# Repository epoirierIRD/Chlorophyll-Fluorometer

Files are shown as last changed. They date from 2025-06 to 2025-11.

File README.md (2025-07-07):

<p align="center">
  ENSSAT Logo
</p>

# Chlorophyll-Fluorometer

## Description

This project aims to develop a portable and low-cost fluorometer for detecting chlorophyll-a concentration, a key indicator of phytoplankton presence. The project is conducted by students in photonics from Enssat in collaboration with the European Institute for Marine Studies (IUEM) and is part of an open-source initiative to facilitate easy and cost-effective replication of the device.

This GitHub repository contains all the necessary resources and instructions for making the device.

The document [Fluoremeter overview](Fluorometer_overview.pdf) aims to provide an overview of the technical aspects of our fluorometer.

## Features

- Measures chlorophyll-a concentration in the range of [1-50] µg/L.
- Low-cost (approximately $200), low-tech, and open-source design.
- Portable

## Principle of fluorometry

<p align="center">
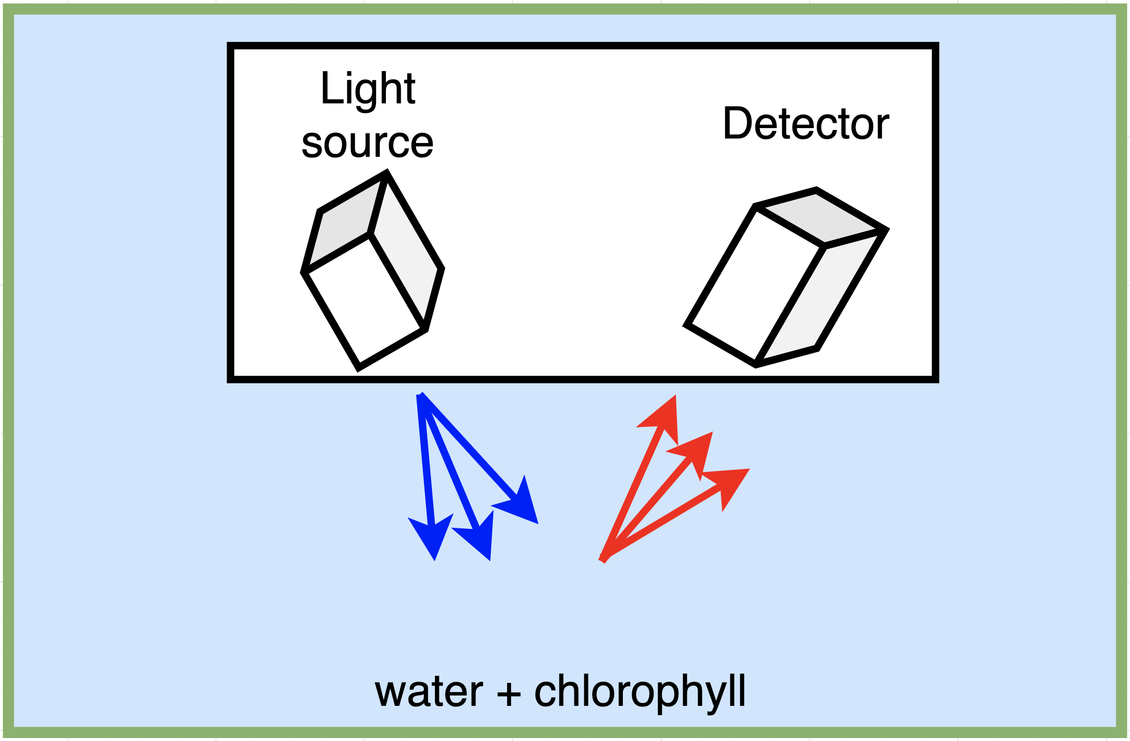
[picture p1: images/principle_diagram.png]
principle diagram
  
</p>

The principle of fluorometry is based on the fact that chlorophyll-a in phytoplankton, when excited by a blue light source at a wavelength of 430 nm, re-emits light in the red spectrum around 670 nm. This red fluorescence is detected by a photodetector, enabling the measurement of chlorophyll-a concentration in the sample.

## Functionality

<p align="center">
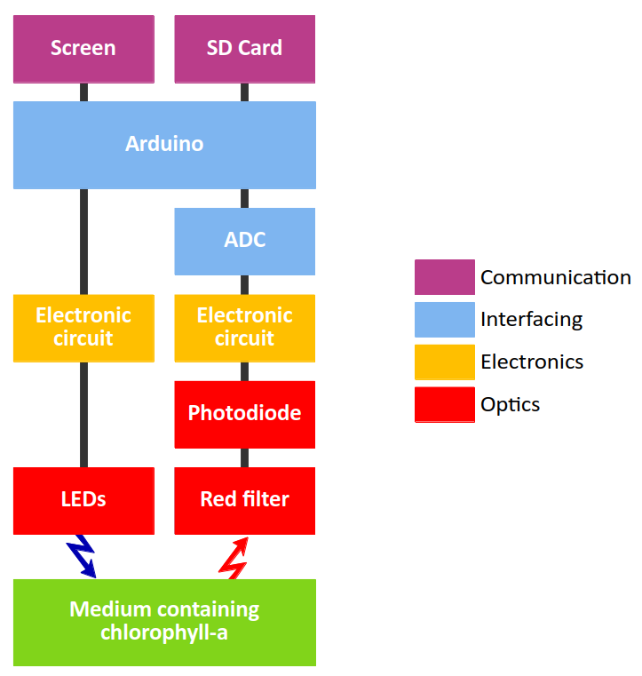
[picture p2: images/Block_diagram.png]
Block diagram
  
</p>

With our setup, high sensitivity is achieved by usind two LEDs and a large-area photodiode to collect more efficiently fluorescence. A red filter is used to prevent the detection of wavelengths other than red. The Arduino board enables modulation and demodulation to eliminate ambient red light.

## Components

The main components are:

| Component | Description |
|-----------|-------------|
| LED | Light Emitting Diode for blue excitation |
| Photodiode | Detects red fluorescence |
| Arduino | Microcontroller for processing |
| ADC | Analog to Digital Converter |
| Transistor | For LED power supply |
| Amplifier | For signal enhancement|
| OLED Screen | Displays values |
| SD Card Shield | Saves values in an SD Card |

For a detailed list of components with the references, please refer to the [Components List](hardware/components.md).

## Construction of the fluorometer

### Prerequisites

- Arduino IDE
- Electronic components
- 3D printer
- Soldering equipment
- Laser cutter

### Installation Steps

1. **Clone the Repository:**

   ```bash
   git clone https://github.com/EnssatPhotonicsProjects/Chlorophyll-Fluorometer.git
   ```

### Assembling the fluorometer

Follow the steps of the [assembly guide](assembly_guide.md) to build the fluorometer.

<p align="center">
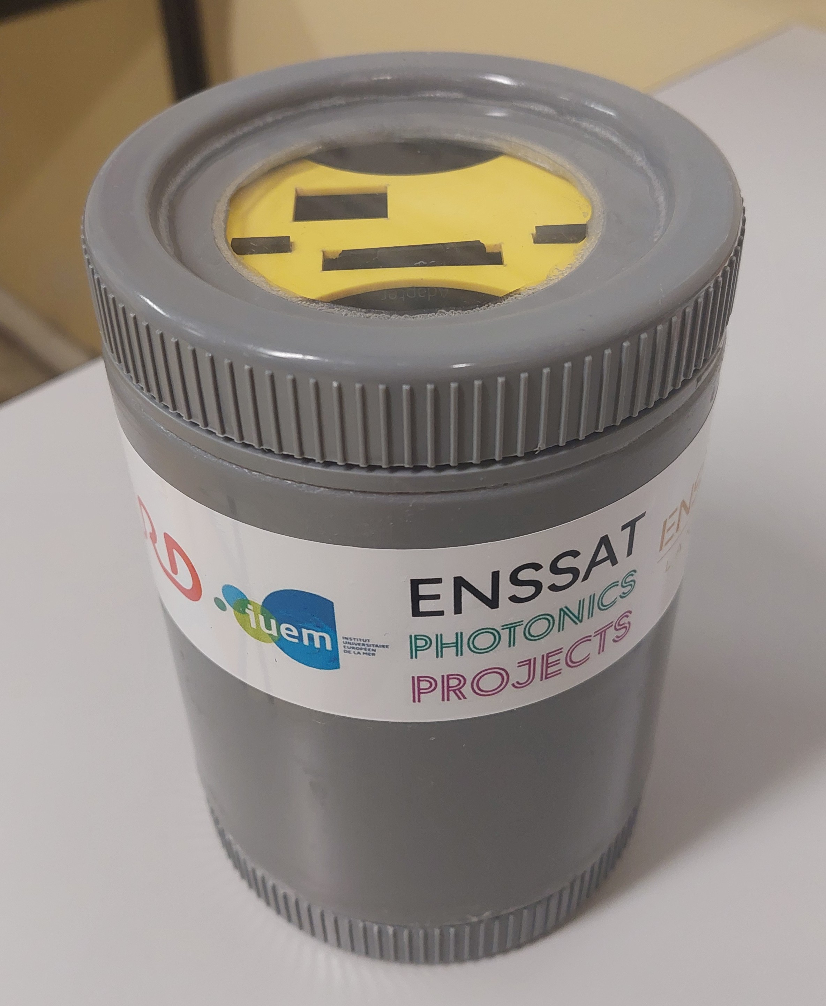
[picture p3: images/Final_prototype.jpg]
Final prototype
  
</p>

## Avenues for Improvement

- The photodiode becomes saturated when used outdoors in bright light.
- The PVC box may not withstand high pressure underwater.

Contributions are welcomed to improve these points.

## To contribute

Contributions to this project are welcomed. Follow this procedure contribute:

1. **Fork the repository** and create your branch:

   ```bash
   git checkout -b my-new-feature
   ```

2. **Make your changes** and test them thoroughly.

3. **Document your changes** in the [EXTERNAL_CONTRIBUTIONS](EXTERNAL_CONTRIBUTIONS.md) file. Begin the file with your name, location and date.

4. **Submit a Pull Request** with a detailed description of your changes.

## Contributors

Team 2024-2025 :
- Loïc Goumarre (minimadcap)
- Cécile Plaçais (CecileP28)
- Agathe Douissard (Douidoui2)
- Olivier Josephiak (Josephiak)
- Mayssame Ismael (Goulgoul1)
- Hugo Le Moal (HugoLeMoal)
- Viken Tevonian
- Merlin Rivière

Team 2023-2024 :
- Jérémy Gigandet
- Brice Hervé
- Thomas Quinchon
- Damien Depauw
- Etienne Chaillot
- Nicolas Chabrier
- Thomas Gysemberg

## Acknowledgments

The authors warmly thank Thierry Chartier, Laurent Bramerie, supervisors of the project at Enssat, Philippe Laborie (Laboratoire de physique corpusculaire, Caen, France) and Etienne Poirier (IUEM, Plouzané, France), members of the steering committee, for their advice and support throughout the project. Special thanks to Etienne Poirier for giving the idea of the project, trusting us and welcome us at IUEM in the last days of the project.

Authors are also very grateful to Antoine Courtay, Hervé Daniel, Clément Dauphin, Hervé Chuberre, teachers at Enssat, and Jean-Philippe Lesault, technician at Enssat, for their advice and technical support. Special thanks to Yvan Guilloit, in charge of the MakerSpace at IUT de Lannion, France, for his help in the integration of the device in the waterproof box.

The fluorometer project started in september 2023 with a first team of Enssat students. Our fluorometer could not have been finalized without their initial work. Many thanks to Nicolas Chabrier, Etienne Chaillot, Damien Depauw, Jérémy Gigandet, Thomas Gysemberg, Brice Hervé, and Thomas Quinchon.

We had the chance to meet Michel Hignette (oceanographer and president of ArmorScience, Lannion, France). We are very grateful to him for sharing his knowledge on phytoplankton.

Hence, we would like to thank Maël Guibré (student at IUT de Lannion) for the time he took to make some videos of the project.

## License

This project is licensed under [CC BY-SA 4.0]. Please see the [`LICENSE`](LICENSE.md) file for more details.

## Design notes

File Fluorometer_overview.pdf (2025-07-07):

# A portable, low-cost, low-tech and open source fluorometer for the measurement of chlorophyll-a concentration

Lo¨ıc Goumarre, C´ecile Pla¸cais, Agathe Douissard, Viken Tevonian, Olivier Josephiak, Mayssame Ismael, Hugo Le Moal and Merlin Riviere

Enssat, 6 rue de Kerampont 22300 Lannion, France, www.enssat.fr, photonics.projects@enssat.fr.

4 July 2025

## 1 Introduction

Chlorophyll-a concentration is a key indicator to estimate the phytoplankton biomass in aquatic ecosystems. Measurements of such concentrations can be made with a fluorometer. Its operating principle is to illuminate the water medium with a blue light and to measure the red fluorescence of chlorophyll-a. However, on today’s market, commercially available fluorometers are quite expensive (several thousands of euros typically) and bulky. For the scientific community, there is a strong need to develop portable and cost-effective solutions, and a very active research is carried out in this area [1, 2, 3, 4, 5].
We are a team of students in photonics at Enssat, Lannion, France, and we took part in a collaborative project between Enssat and the Institut Universitaire Europ´een de la Mer (IUEM, European Institute For Marine Studies). This project meets IUEM’s need to create a portable, low-cost, low-tech, and open source chlorophyll-a concentration sensor. The highly-sensitive device we have successfully developped is affordable (around 200 e) and easily reproducible thanks to the detailed documentaton available on GitHub [6].
The present document aims to provide an overview of some technical aspects of our fluorometer. It first presents the background and specific requirements of the project (defined in collaboration with the IUEM). The design of the fluorometer is then presented, with separate sections in optics, electronics and interfacing. Finally, we present the results of tests carried out with our fluorometer.

## 2 Needs

The IUEM provided us detailed specifications describing the needs and requirements for the development of the fluorometer. This sensor had to be portable, low-cost, low-tech and open source. The specifications served as the basis for guiding the design and the development of the chlorophyll-a concentration sensor, meeting standard requirements for environmental monitoring.
The technical specifications expected for the sensor in terms of metrology were the following:
Range | [0.1-50] µg/L
Measurement sensitivity | 0.1 µg/L
Measurement error | < 0.2 µg/L

The electronical specifications were:

Measurement rate | 10 sec
Response time | 1 sec
Alimentation | 3.3 V, 5 V or 12 V
Data output protocol | I2C, UART or analog

## 3 General principle

When chlorophyll-a is excited by a blue light source at a wavelength of about 430 nm, it re-emits light in the red spectrum around 670 nm. This red fluorescence is collected by a photodetector, enabling the concentration of chlorophyll-a to be measured. Figure 1(a) illustrates the absorption and emission spectrum of chlorophyll-a, and figure 1(b) shows a schematic diagram of a fluorometer.

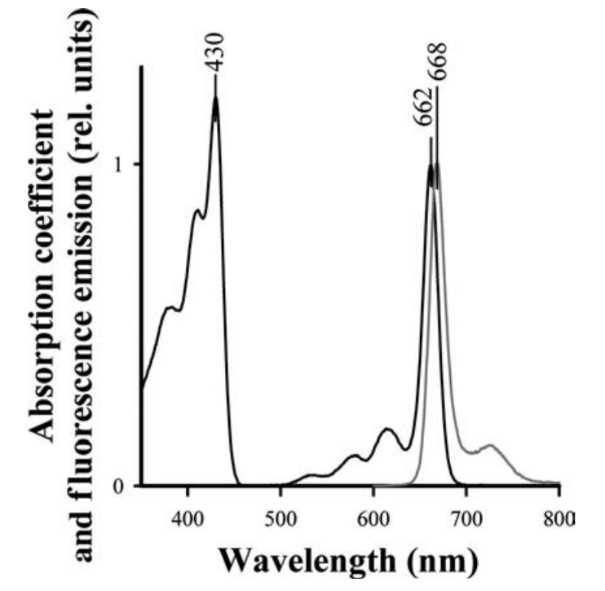
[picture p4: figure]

(a) Absorption and emission spectrum of chlorophyll-a.

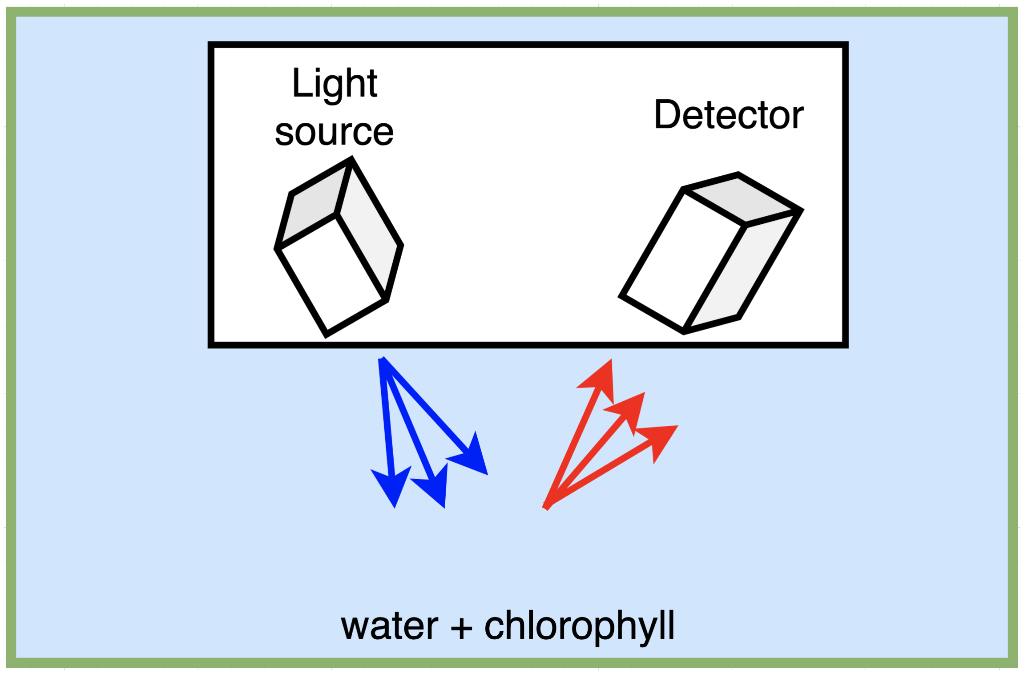
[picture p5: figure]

(b) Schematic diagram of a fluorometer.

Figure 1: Principle of fluorimetry with chlorophyll-a.

## 4 Fluorometer conception

### 4.1 Block diagram

Figure 2 illustrates the block diagram of our fluorometer. Blue LEDs illuminate the water medium containing chlorophyll-a. A photodiode detects the red fluorescence of chlorophyll-a through a red filter used to prevent the detection of light at other wavelengths than red. The Arduino board enables modulation and demodulation to eliminate ambient red light.

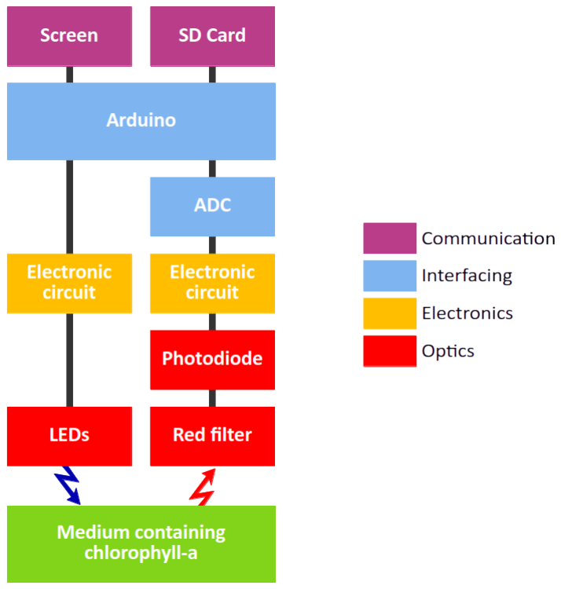
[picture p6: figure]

Figure 2: Block diagram.

The different parts shown in the block diagram of figure 2 will now be detailed.

### 4.2 Optical part

The optical part of our project is divided into two sub-parts : emission and reception.

### 4.2.1 Emission

As explained previously, a blue LED is needed to make a chlorophyll-a fluoremeter. We actually used two LEDs to double the available optical power. Specifications of the LEDs are given in table 1.

Reference | Luxeon C Color Line - Violet
Peak wavelength | 424 nm (measured)
Spectral half-width | 20 nm
Typical viewing angle | 165°
Typical power | 600 mW

Table 1: Specifications of the blue LEDs.

Due to their large viewing angle, we performed measurements to find the optimum angle between the LEDs and the photodiode. Figure 3 shows the measured voltage on the photodiode as a function of the angle between one LED and the photodiode in an experimental setup similar to figure 1(b). It shows that the optimal angle is around 30°. In the following, the photodiode will be positioned parallel to the air-water interface and the two LEDs will be on either side of the photodiode at an angle of 30°, as depicted later in figure 5.

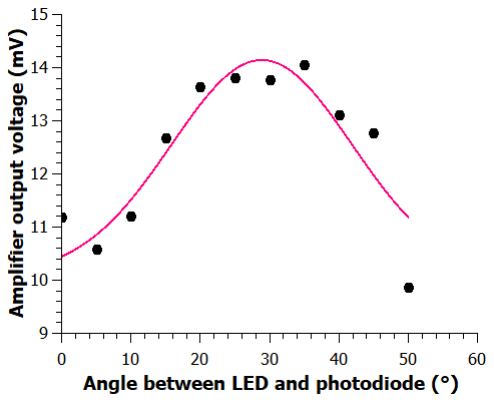
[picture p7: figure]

Figure 3: Amplifier output voltage on the photodiode as a function of the angle netween the LED and the photodiode.

### 4.2.2 Reception

Once the chlorophyll-a is stimulated with blue light, it fluoresces red light. This red light is collected by a photodiode positioned against the transparent window of the fluorometer to capture maximum fluorescence. A photodiode with a large area maximizes the collected light. However, it is also important to take into account the dark current of the photodiode. The dark current must be sufficiently low to detect low chlorophyll concentrations. The specifications of the choosen photodiode are presented in table 2.

Reference | Thorlabs FDS10X10
Dark current | 200 pA
Surface | 100 mm²

Table 2: Specifications of the photodiode.

Three layers of a red filter are placed in front of the photodiode to filter out other wavelengths than red. The red filter we use is a light filter used by lighting technicians in the entertainment industry. Its specifications are described in table 3. The transmission spectrum of the filter is shown in figure 4. The red filter of 3D glasses can also be used for example.

Reference | Lee Filters 164 Flame Red
Colour temperature | 6774 K
Transmission at 424 nm | 3 %
Transmission at 670 nm | 79 %

Table 3: Specifications of the red filter.

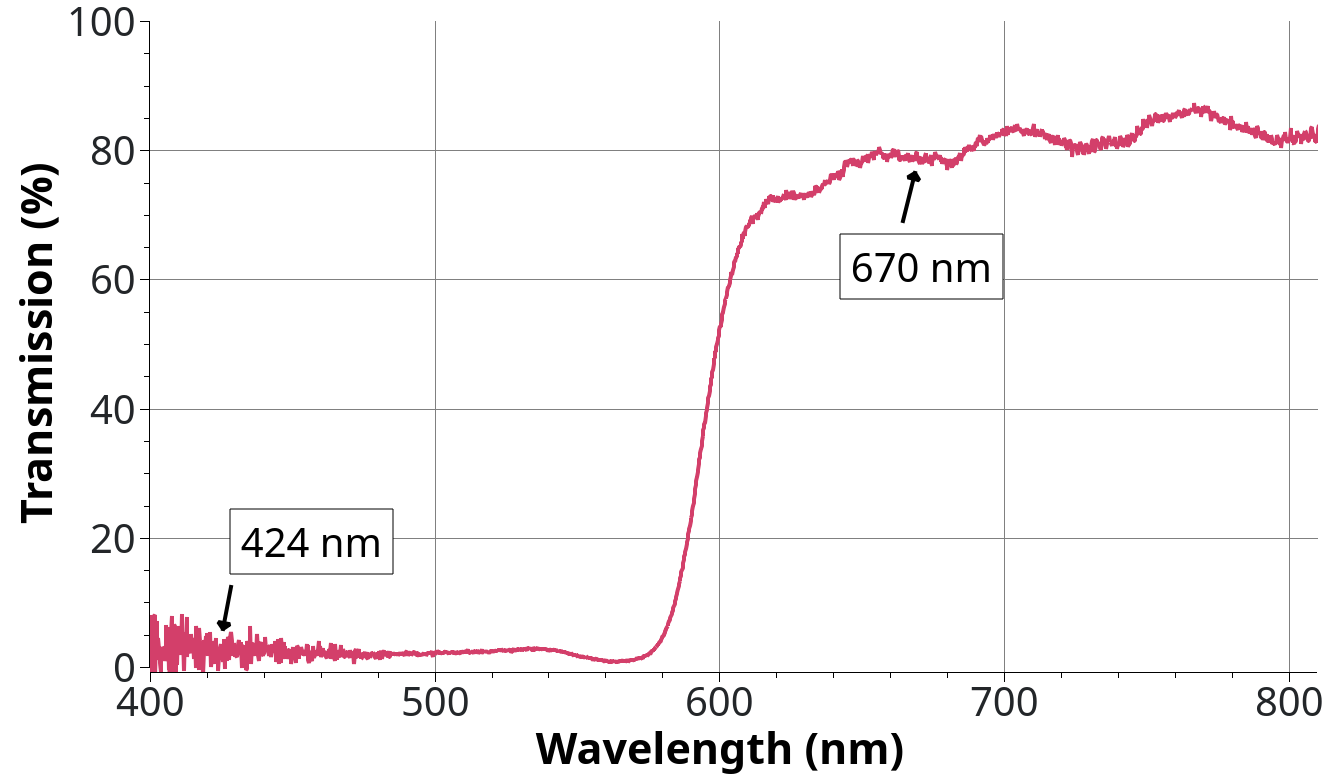
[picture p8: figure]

Figure 4: Transmission spectrum of the red filter.

The final setup for the optical components is shown in Figure 5.

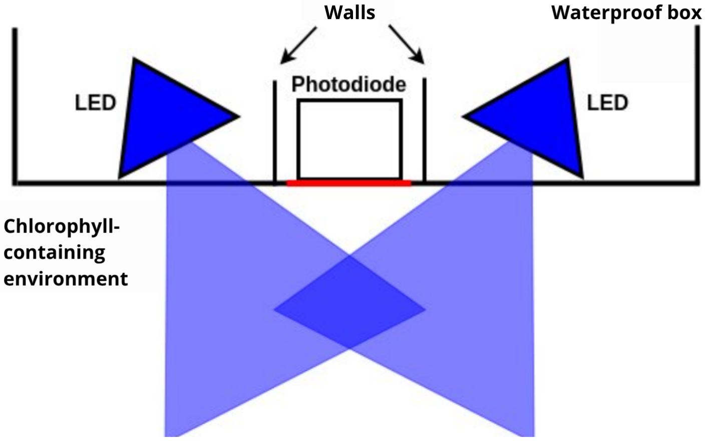
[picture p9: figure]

Figure 5: Final configuration of the optical components.

### 4.3 Electronical part

In this section, we describe the different electronic circuits present in our device.

### 4.3.1 LEDs alimentation

First, the two LEDs have to be powered with a current of 400 mA each. To do that, we propose the electric circuit of figure 6. The transistor provides the current that powers the LEDs. It is controlled by the desired voltage. The transistor transforms this voltage into a current that is shared equally between the two LEDs. The specifications of the transistor are presented in table 4.

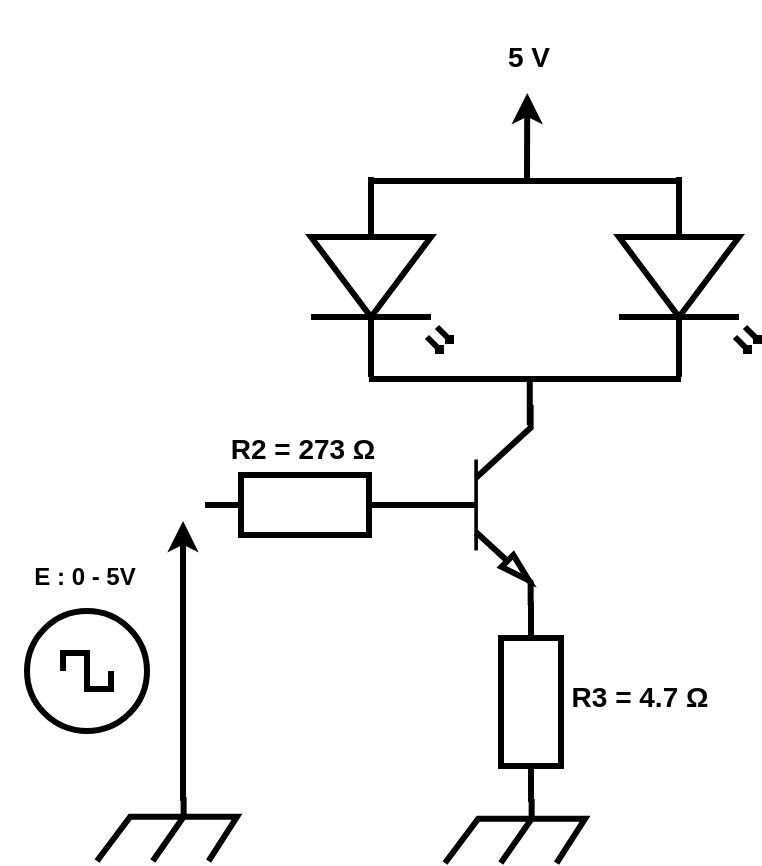
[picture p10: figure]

Figure 6: Circuit diagram of the LEDs alimentation.

Reference | PN2222
Type | BJT n-type
VCE (sat) | 1 V
VBE (sat) | 2 V
hFE | between 100 and 300

Table 4: Specifications of the transistor.

### 4.3.2 Transimpedance amplifier

For the receiving part of the device, the transimpedance amplifier of figure 7 is proposed. Thanks to this amplifier, the photodiode current is converted into a voltage up to Vmax = 5 V in order to be read by an analog-to-digital converter (ADC). The amplifier gain corresponds to the value of R1 and is 10⁵ V/A in our case. This indicates that the maximum measurable photocurrent is Imax = Vmax/R1 = 50 µA. In the absence of additionnal noise source, the minimum measurable photocurrent is theoretically the dark current of the phototodiode, i.e. 200 pA in our case.

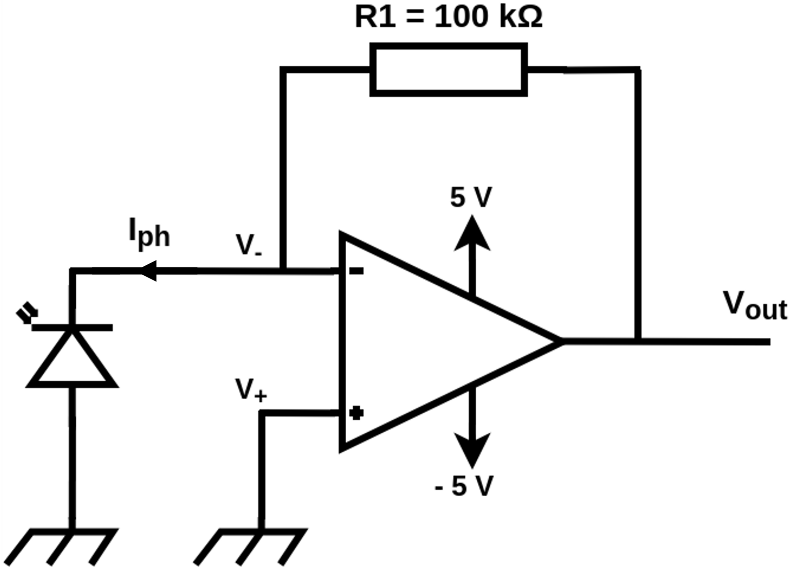
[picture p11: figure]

Figure 7: Circuit diagram of the transimpedance amplifier.

### 4.3.3 Generation of −5/0/+5 V

Self-sufficient power supply (typically a powerbank) can be ideal to power the fluorometer. However, this kind of battery provides only a 0-5 V voltage. To generate the −5/0/+5 V voltage needed by the operational amplifier of figure 7, we use the switched capacitor voltage converter (MAX660) shown in figure 8.

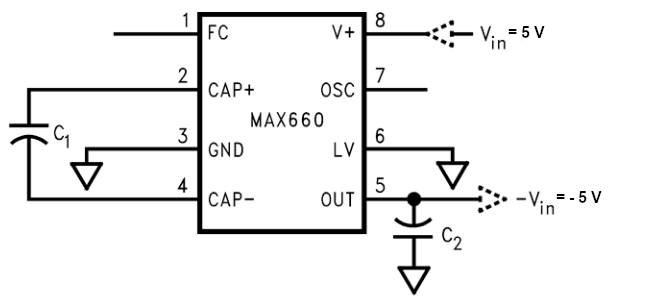
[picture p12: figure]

Figure 8: Switched capacitor voltage converter (MAX660) for −5/0/+5 V generation.

### 4.4 Interfacing part

### 4.4.1 Modulation of the LEDs

The blue light emitted by the LEDs is on-off modulated by the Arduino at a frequency of 100 Hz and a duty cycle of 1/2. This modulation is maintained during 1 s, then the LEDs are switched off for 9 s. The time diagram of the modulation scheme is shown in figure 9. The modulation frequency of the LEDs is limited by the execution time of the Arduino program.

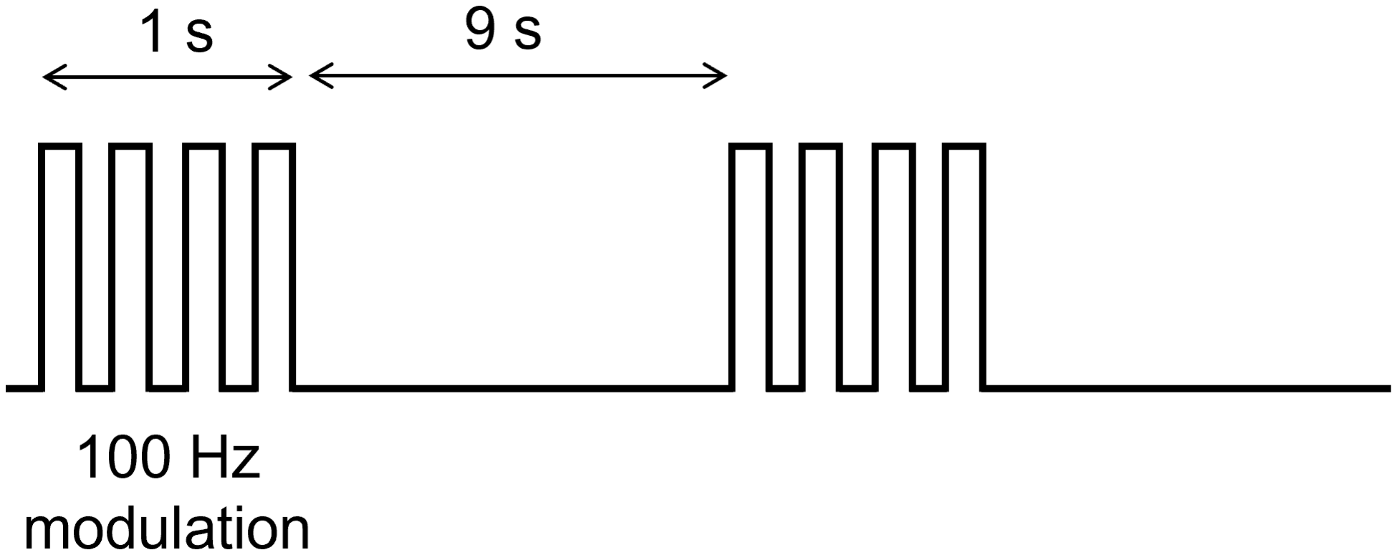
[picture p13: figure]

Figure 9: Modulation time diagram.

### 4.4.2 Analog-to-digital conversion

The Arduino board we use is the UNO R3. Its internal ADC is a 12-bit ADC. To increase the resolution of our fluorometer, we prefer to use an external ADC (ADS 1115) with a 16-bit sampling. Thus, the resolution of the fluorometer is 76 µV per bit, corresponding to 0,76 nA per bit.

### 4.4.3 Demodulation

To demodulate the signal, the program reads the photodiode voltage during both the on-state and the off-state of the LEDs during the flashing phase of 1 s. Then it substracts the off-state voltage Voff from the on-state voltage Von in order to eliminate the ambiant red light. This ensures to measure only the fluorescence of the chlorophyll due to the blue excitation. Figure 10 summaries the demodulation process.

Then the programme averages the 100 values calculated during the 100 periods of the flashing phase and returns one single value of photocurrent every 10 s.

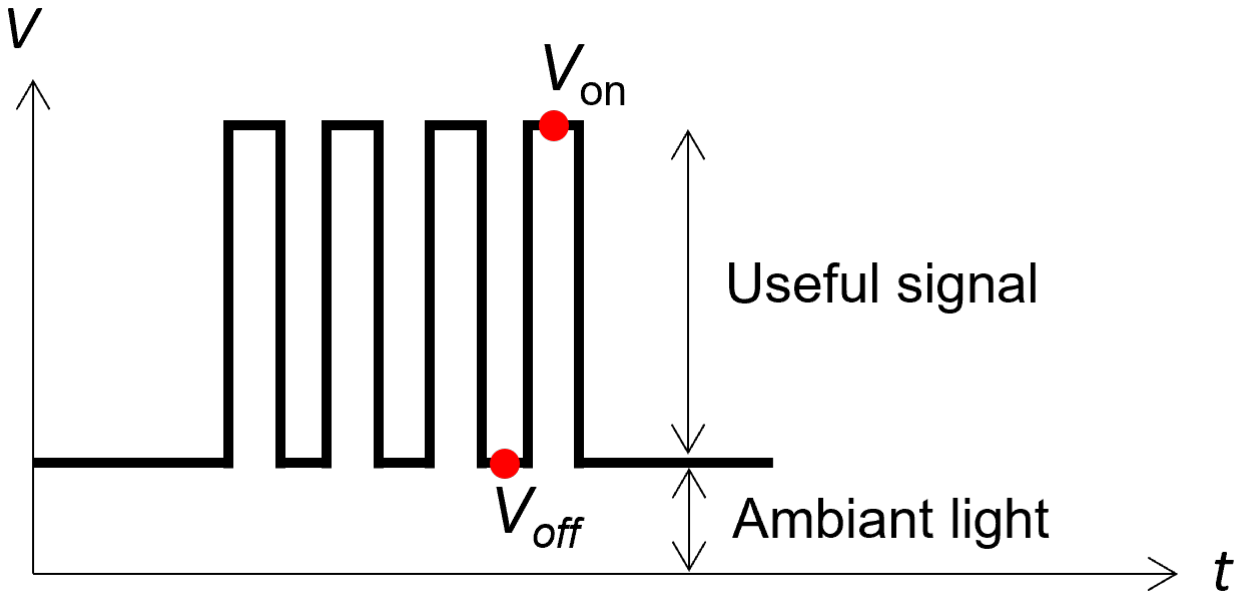
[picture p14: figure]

Figure 10: Demodulation of the received signal.

### 4.4.4 Display and storage

A OLED screen is added to facilitate interactions with the users. It displays the values of the measured photocurrent in nA.
A SD card shield is also added for long-term recording. The photocurrent values, as well as the time of measurement, are recorded on the SD card in the form of a text file, as shown in figure 11.

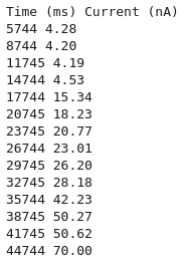
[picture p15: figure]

Figure 11: Text file recorded on the SD card.

### 4.5 Final diagram

The global circuit diagram of the fluorometer is shown in figure 12.

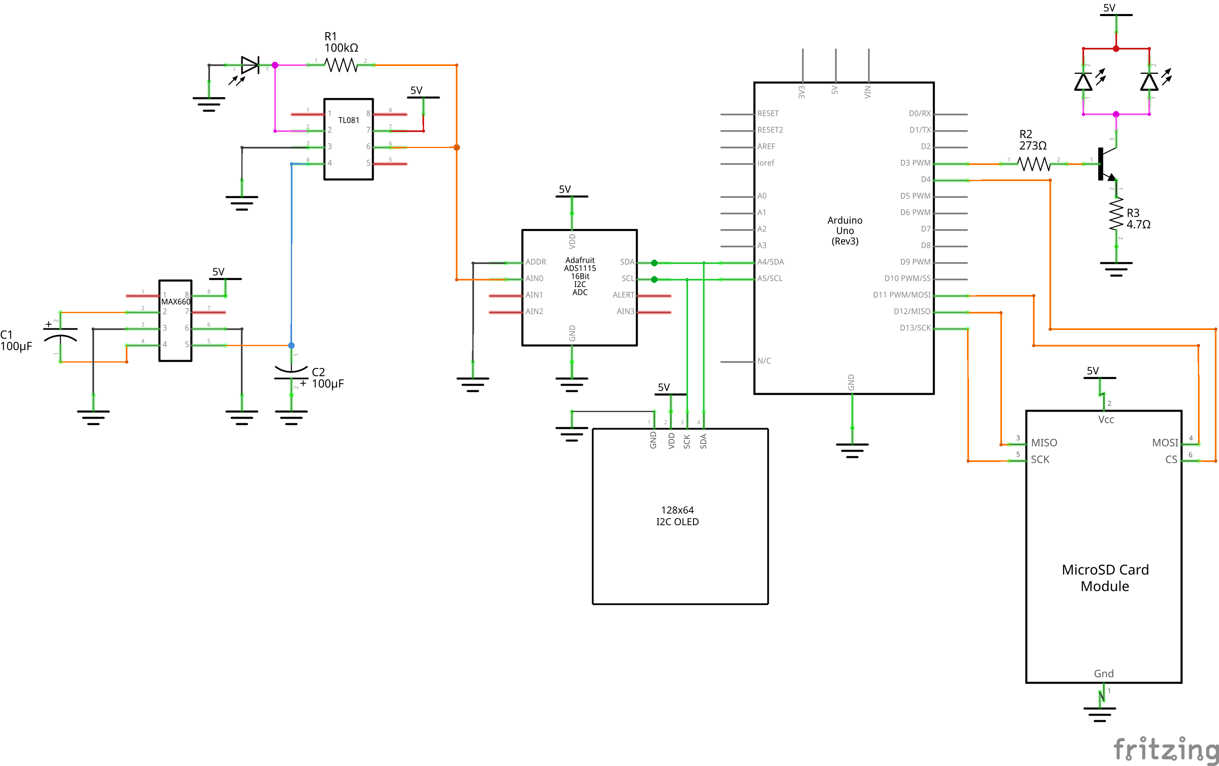
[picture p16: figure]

Figure 12: Fluorometer’s global circuit diagram.

### 4.6 Final Assembly

The fluorometer is assembled in a PVC tube. Access plugs are glued to the ends of a sleeve. The caps are cut out and a transparent plate of PMMA plastic is glued on to let the light going through. The inner structure that holds the Arduino and the circuit board is made in black PMMA and cut with a laser cutter. Spacers are used to strengthen the structure. The holder for the LEDs and the photodiode is 3D-printed and screwed to the structure. A powerbank is added in the box for the autonomy of the system.
The bottom cap is glued and cannot be opened. The top cap can be opened and the structure is easy to remove in order to recharge the powerbank, take the SD card, load a program on the Arduino or replace a component. The complete box is waterproof. Yet, PVC box may not withstand high pressure underwater.

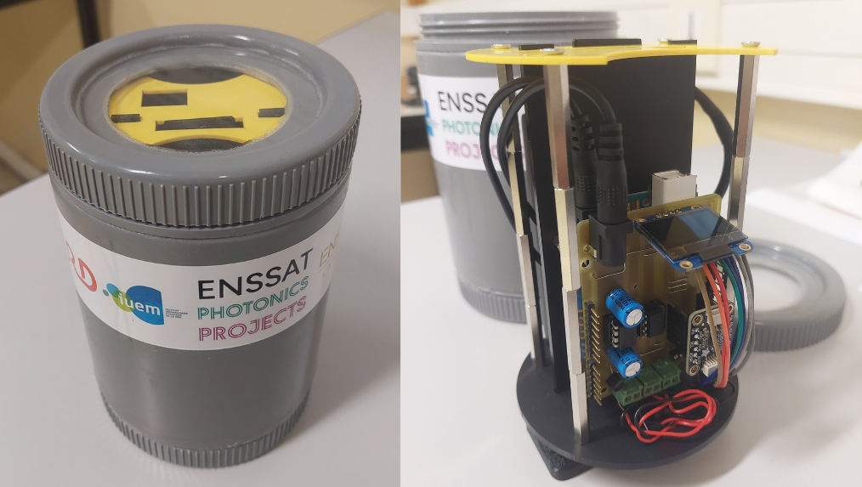
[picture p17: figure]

Figure 13: Photos of the prototype.

## 5 Tests and results

A series of tests were carried out to caracterize and calibrate the fluorometer.

### 5.1 Measurements with spinach chlorophyll-a

Firstly, measurements of solutions of chlorophyll-a extracted from spinach leaves have been made. The spinach chlorophyll-a was extracted following this method : spinach leaves have been shredded and the chlorophyll-a filtered using 96% ethanol. Then the concentration has been measured with a spectrometer thanks to the formula demonstrated in [7]. These measurements were done in a dark room. The results are shown in figure 14.

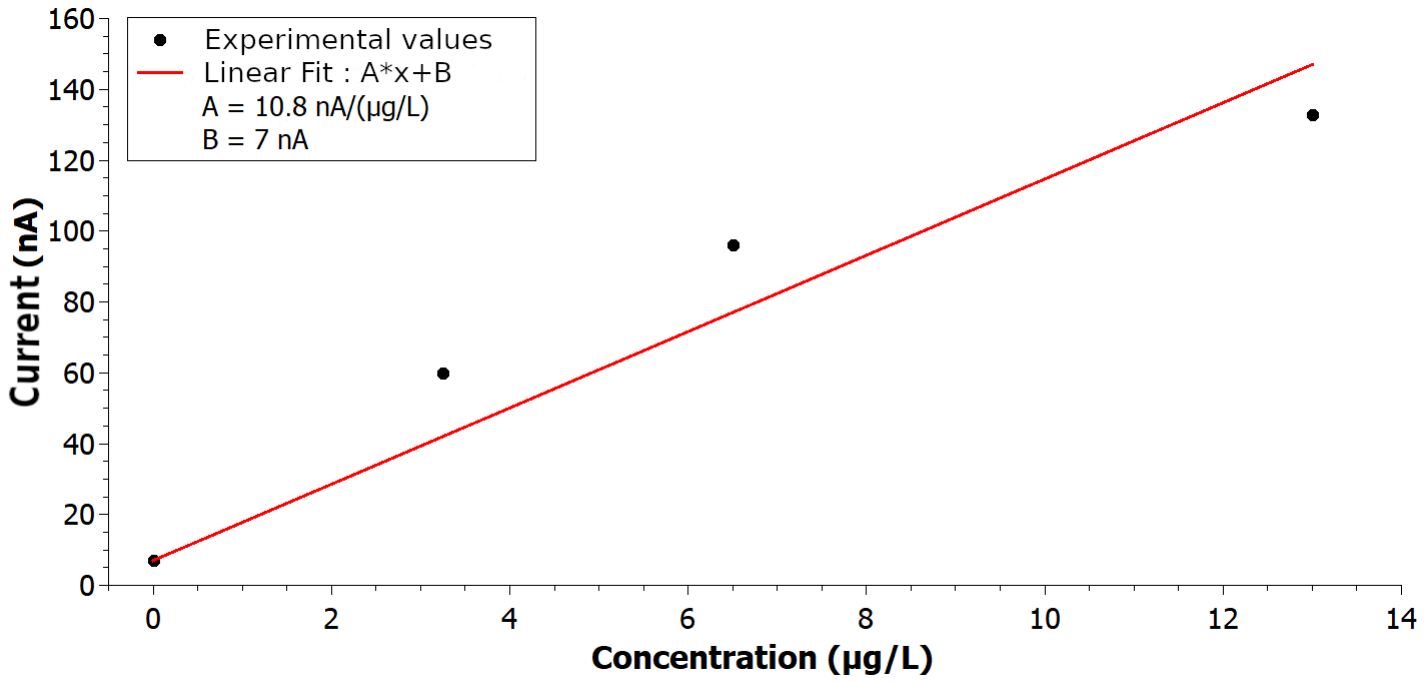
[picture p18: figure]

Figure 14: Calibration of the fluorometer with spinach chlorophyll-a.

This calibration shows that the fluorometer can measure low concentrations of chlorophyll. The first point, corresponding to 7 nA, is a measurement in clear water. This gives the detection threshold of our prototype. This value is not the 200 pA dark current of the photodiode because of other noise sources (due do electronics for example).

### 5.2 Measurements with phytoplankton

Then, measurements of solutions of phytoplankton have been run with our fluorometer. A highly concentrated phytoplankton solution has been diluted. Values of concentration were measured with a commercial fluorometer (the RBRtridente) and the corresponding current was read on our low-cost fluorometer. Figure 15 shows the results.

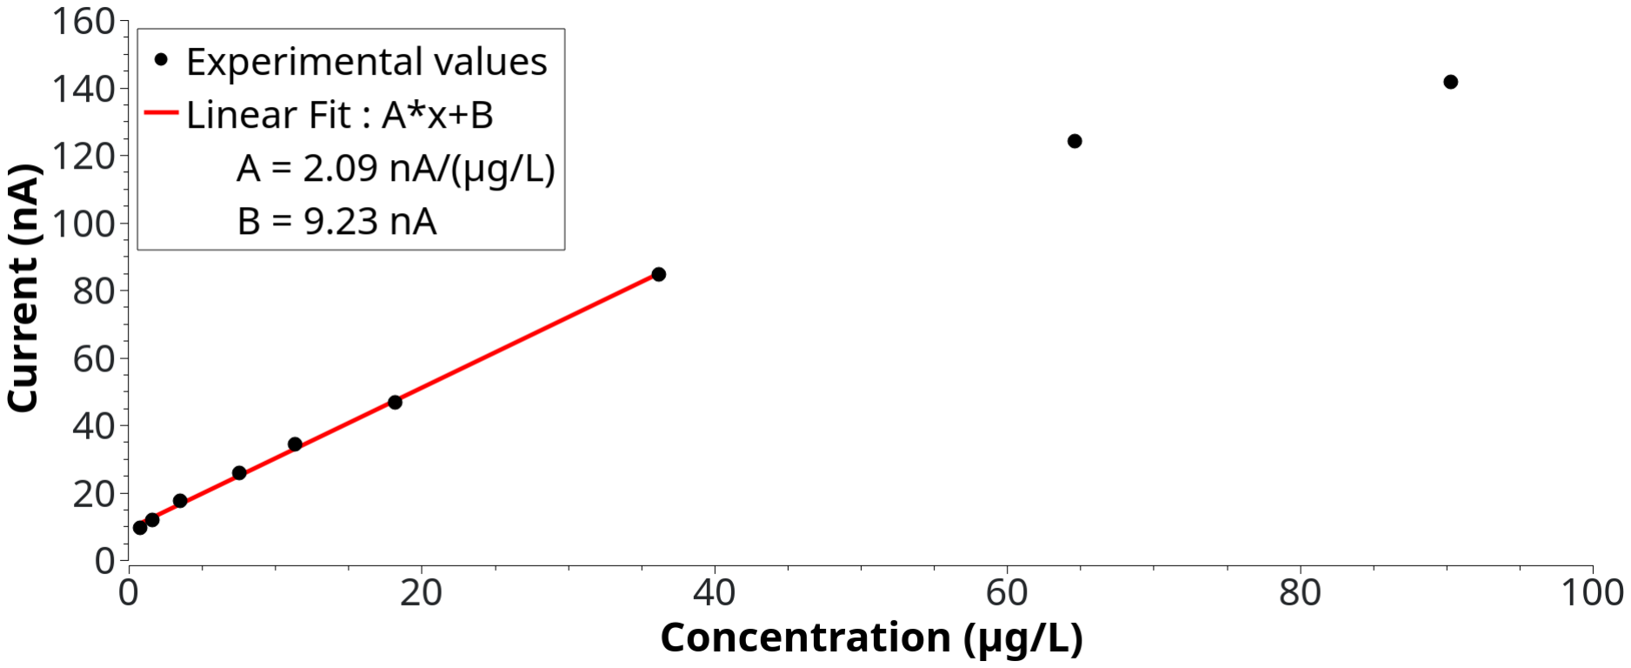
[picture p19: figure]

Figure 15: Calibration of the fluorometer with phytoplankton.

The fluorometer operates linearly over a range from 1 to 50 µg/L. The interesting point is that our fluorometer can measure chlorophyll-a concentrations as low as 1 µg/L under experimental laboratory conditions. The prototype is limited to indoor use, as the photodiode saturates outdoors in bright light.

## 6 Conclusion

During this project, we have realised a fluorometer for chlorophyll-a concentration measurements. This fluorometer is portable, low-cost and low-tech. It can be completely reproductible thanks to a public GitHub repository [6].
Our fluorometer can measure chlorophyll-a concentrations as low as 1 µg/L. This performance is achieved thanks to the use of two blue LEDs illuminating a large volume of water and a large-area photodiode with a low dark current. Our fluorometer is simple, low-cost (around 200 e) and easy to make thanks to the use of standard components. In the context of global warming, the need to measure phytoplankton is crucial. Portable and low-cost solutions might play a very important role in the future for diagnosing the ecological status of aquatic environments. We sincerely hope that our solution can help the scientific community, and would be delighted to make a small contribution to environmental protection through the study of coastal zones.

## Acknowledgments

The authors warmly thank Thierry Chartier, Laurent Bramerie, supervisors of the project at Enssat, Philippe Laborie (Laboratoire de physique corpusculaire, Caen, France) and Etienne Poirier (IUEM, Plouzan´e, France), members of the steering committee, for their advice and support throughout the project. Special thanks to Etienne Poirier for giving the idea of the project, trusting us and welcome us at IUEM in the last days of the project.
Authors are also very grateful to Antoine Courtay, Herv´e Daniel, Cl´ement Dauphin, Herv´e Chuberre, teachers at Enssat, and Jean-Philippe Lesault, technician at Enssat, for their advice and technical support. Special thanks to Yvan Guilloit, in charge of the MakerSpace at IUT de Lannion, France, for his help in the integration of the device in the waterproof box.
The fluorometer project started in september 2023 with a first team of Enssat students. Our fluorometer could not have been finalized without their initial work. Many thanks to Nicolas Chabrier, Etienne Chaillot, Damien Depauw, J´er´emy Gigandet, Thomas Gysemberg, Brice Herv´e, and Thomas Quinchon.
We had the chance to meet Michel Hignette (oceanographer and president of ArmorScience, Lannion, France). We are very grateful to him for sharing his knowledge on phytoplankton.

Hence, we would like to thank Ma¨el Guibr´e (student at IUT de Lannion) for the time he took to make some videos of the project.

## References

[1] T. Leeuw et al., In situ Measurements of Phytoplankton Fluorescence Using Low Cost Electronics, Sensors, Vol. 13, pp. 7872–7883 (2013). https://www.mdpi.com/1424-8220/13/6/7872.
[2] Harvey Bates et al., A guide to Open-JIP, a low-cost open-source chlorophyll fluorometer, Photosynthesis Research, Vol. 142, pp. 361–368 (2019). https://doi.org/10.1007/s11120-019-00673-2.
[3] L. R. C. S´a, et al., Portable and Low-Cost Fluorometer for Phytoplankton Monitoring, 2023 IEEE 7th Portuguese Meeting on Bioengineering (ENBENG), pp. 96–99 (2023). https://ieeexplore.ieee.org/document/10175351.
[4] R. Sanchez Olvera, D´eveloppement d’une sonde multiparam`etres `a bas coˆut pour les eaux marines et continentales, Th`ese de doctorat de l’Universit´e Toulouse III - Paul Sabatier (2024). https://theses.fr/2024TLSES108.
[5] X. Chen et al. A low-cost and portable fluorometer based on an optical pick-up unit for chlorophyll-a detection, Talanta, Vol. 269, pp. 125447. https://doi.org/10.1016/j.talanta.2023.125447.
[6] https://github.com/EnssatPhotonicsProjects/Chlorophyll-Fluorometer.
[7] J.F.G.M. Wintermans and A. De Mots, Spectrophotometric characteristics of chlorophylls a and b and their pheophytins in ethanol, Biochimica et Biophysica Acta (BBA) - Biophysics including Photosynthesis, Vol. 109, pp. 448-453 (1965). https://doi.org/10.1016/0926-6585(65)90170-6.


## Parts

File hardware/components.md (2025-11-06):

# List of components for EU based project

## Electronic components

| Component | Manufacturer - Ref | Seller - Ref | Quantity | Price per unit (€) |
|-----------|---------------------|--------------|----------|--------------------|
| Photodiode | Thorlabs - FDS10X10 | [Thorlabs - FDS10X10](https://www.thorlabs.com/thorproduct.cfm?partnumber=FDS10X10) | 1 | 122 € |
| Arduino | ARDUINO UNO SMD R3 ATMEGA328 - A000073 | [Mouser - A000073](https://www.mouser.fr/ProductDetail/782-A000073) | 1 | 22 € |
| ADC 16 bits | ADS1115 Adafruit I2C - ADA1085 | [GoTronic - 31893](https://www.gotronic.fr/art-module-4-canaux-analogiques-i2c-ada1085-21114.htm) | 1 | 19.90 € |
| LED[¹] | Luxeon C Color Line - Violet 420-430 nm L1C1-VLT1000000000 | [LED-Supply, Vermont USA](https://www.ledsupply.com/leds/luxeon-c-color-leds) | 2 | 6 $ |
| Red Filter | Lee Filters - 182 Light Red | [La BS - FL182](https://www.la-bs.com/ArticleDetails.aspx?Code=FL182) | 1 | 20 € |
| Transistor | PN2222A TRANS NPN 40V 0.8A TO-92-3 PN2222A PBFREE | [Mouser 610-PN2222A](https://www.mouser.fr/ProductDetail/610-PN2222A) | 1 | <1 € |
| Operational amplifier | TL081 | [Mouser - 595-TL081CP](https://www.mouser.fr/ProductDetail/595-TL081CP) | 1 | <1 € |
| 8 contacts socket | IC & Component Socket, 8 Contacts, DIP Socket, 2.54 mm, 7.62 mm, Copper Alloy, DILB8P-223TLF | [ Farnell - 2668407 ](https://fr.farnell.com/en-FR/amphenol-icc-fci/dilb8p-223tlf/dip-socket-8pos-2row-2-54mm-th/dp/2668407) | 2 | 0.2 € |
| Wire-To-Board Terminal Block | 3.5 mm, 2 Ways, 30 AWG, 16 AWG, 1.5 mm², Screw, Phoenix 1751248 | [Farnell - 2478586](https://fr.farnell.com/en-FR/phoenix-contact/mkds-1-2-3-5/tb-wire-to-brd-2pos-16awg/dp/2478586) | 3 | 1.3 € |
| Voltage converter | MAX660 MAX660CPA+ | [Mouser 700-MAX660CPA](https://www.mouser.fr/ProductDetail/700-MAX660CPA) | 1 | 8.39 € |
| Resistors 100 kΩ brown black yellow gold | Through Hole Resistor, 100 kohm, 250 mW, ± 1%, Axial Leaded, 250 V| [Farnell - 9341129](https://fr.farnell.com/en-FR/multicomp-pro/mf25-100k/res-100k-1-0-25w-axial-metal-film/dp/9341129) | 1 | 0.10 € |
| Resistors 270 Ω red violet brown gold | Through Hole Resistor, 270 ohm, MCF Series, 250 mW, ± 5%, Axial Leaded, 250 V, MCF 0.25W 270R | [Farnell - 9339353](https://fr.farnell.com/en-FR/multicomp-pro/mcf-0-25w-270r/res-270r-5-250mw-axial-carbon/dp/9339353) | 1 | 0.04€ |
| Resistors 4.75 Ω +/- 1% yellow violet green silver brown | Through Hole Resistor, 4.7 ohm, MF25 Series, 250 mW, ± 1%, Axial Leaded, 250 V, MF25 4R7 | [Farnell - 9341994](https://fr.farnell.com/en-FR/multicomp-pro/mf25-4r7/res-4r7-1-250mw-axial-metal-film/dp/9341994) | 1 | 0.12 € |
| Capacitor 150 μF, 16V | Electrolytic Capacitor, 150 µF, 16 V, ± 20%, Radial Leaded, 2000 hours @ 105°C, Polar | [Farnell - 3131982](https://fr.farnell.com/wurth-elektronik/860020373008/condensateur-150uf-16v-alu-elec/dp/3131982) | 2 | 0.16€ |
| OLED Screen 128x64 Dot Matrix | DFRRobot DFR0650 SSD1306 | [Mouser - DFR0650](https://www.mouser.fr/ProductDetail/DFRobot/DFR0650?qs=vmHwEFxEFR9nN6dqGZZLUA%3D%3D) | 1 | 13.05 € |
| SD Card Shield | TRU COMPONENTS TC-8579888 | [GoTronic - 28506](https://www.gotronic.fr/art-module-carte-sd-gt126-28506.htm) | 1 | 9.49 € |
| Powerbank[²] | Output 5 V - 2.4 A, dim. 100 x 50 x 25 mm max | [VRURC 2000mAh mini power bank](https://www.amazon.fr/gp/product/B099F29H7Y?smid=A2BNE5LRDUXQ6R&th=1) | 1 | 30 € |
| Alimentation cable part 1 | Power splitter 5.5 x 2.1 mm CA50-2 | [Gotronic 49105](https://www.gotronic.fr/art-dedoubleur-d-alimentation-5-5-x-2-1-mm-ca50-2-24581.htm) + angled USB plug (homemade) | 1 | 2.65 € |
| Alimentation cable part 2 | USB cable male A right angled + USB male A | [TL494-ND Digikey UR020-006-RA](https://www.digikey.fr/fr/products/detail/eaton-tripp-lite/UR020-006-RA/4767696) | 1 | 7.85 € |
| DC Power Connector| DC10A, Jack, 5 A, 2.1 mm, PCB Mount, Solder, CLIFF FC68148  | [Farnell 224959](https://fr.farnell.com/en-FR/cliff-electronic-components/fc68148/conn-dc-power-jack-2-1mm-5a-12v/dp/224959?CMP=GRHB-OCTOPART) | 1 | 6.57 € |

[¹]LED-Supply does not have a reseller in Europe for integrated LED on PCB. LED and PCB(eval-board) can be bought separately from European reseller and assembled. References to come shortly  
[²]Several options are possible for the power bank, Lipo battery,... geometric dimensions are critical due to littel space available. Beware, there is litlle power demand and some powerbanks shut down automatically.

## Case and support

| Component | Reference | Quantity | Price per unit |
|-----------|-----------|----------|----------------|
| Filament PLA black | / | **not determined** | ≈5 € |
| PVC sleeve | 100 mm diameter | 1 | 2 € |
| PVC plug | 100 mm diameter | 2 | 7.58 € |
| Transparent PMMA thickness 3 mm | / | ~400 cm² | 2 € |
| Matt black PMMA thickness 3 mm | / | ~180 cm² | 1 € |
| PMMA thickness 2 mm | / | ~100 cm² | <1 € |
| Screws, nuts, washers, spacers | / | ~50 pcs | 10 € |

## Final price

The price is estimated in **June 2025** at **230 $ without delivery**.

The price is estimated in **July 2025** at **300 € without delivery**.

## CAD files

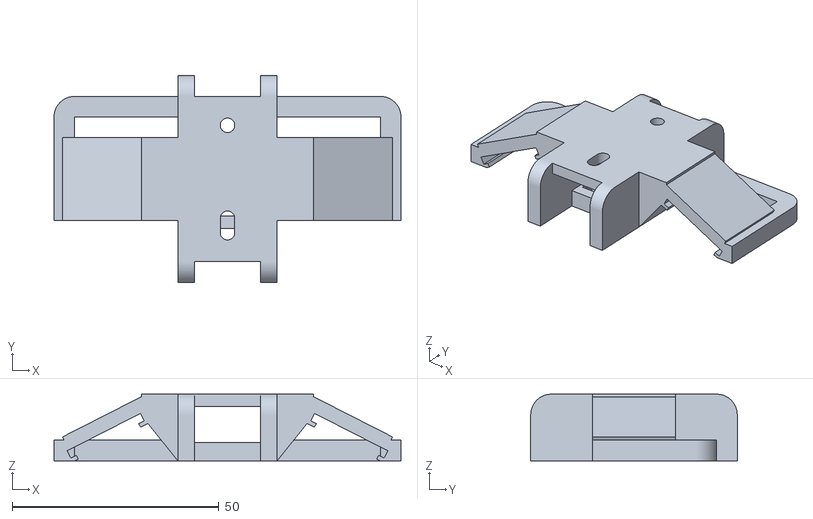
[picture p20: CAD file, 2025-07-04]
hardware/3D_ready_to_print_LED-Photodiode-Support.stl
84.0 x 50.0 x 16.2

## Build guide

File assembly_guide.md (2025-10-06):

# Assembly Guide for Chlorophyll-Fluorometer

This guide provides detailed instructions on how to assemble the Chlorophyll-Fluorometer device.

## Prerequisites

Before starting the assembly process, ensure you have the following tools and components ready:

- Arduino IDE installed on your computer
- All electronic components listed in the [Components List](hardware/components.md)
- 3D printer for printing support structures
- Soldering equipment for assembling electronic circuits
- Basic hand tools (screwdrivers, pliers, etc.)

## Step 1: Clone the Repository

To get started, clone the project repository to your local machine:

```bash
git clone https://github.com/EnssatPhotonicsProjects/Chlorophyll-Fluorometer.git
```

## Step 2: Assemble the Electronic Components

### Using a Breadboard

If you are prototyping or prefer not to use a PCB, you can assemble the circuit on a breadboard. Refer to the [Circuit-diagram.pdf](hardware/Circuit-diagram.pdf) for detailed connections.

### Using a PCB

1. Download the PCB design file from the repository: [PCB File](hardware/Fluorometer_PCB/).
2. Order the PCB from a manufacturer or print it if you have the necessary equipment. For example, go to [JLCPCB](https://jlcpcb.com/), and in the field "Add gerber files" drop a zip of the folder /CAMoutputs situated at [this location](hardware/Fluorometer_PCB/).
You will receive a quality pro PCB and you can even choose the color.
3. Solder the components onto the PCB following the schematic diagram. 
Tip: As you will solder with you PCB upside down, start with the thin components (resistors,...) and finish with the thick ones (headers, capacitor, ...).

## Step 3: Assemble the Support Structures

Use the provided STL file to 3D print the necessary support structures with black PLA filament, and a filling density of 50%. Printing takes about 7 hours : 

- [LED and Photodiode Support](hardware/3D_ready_to_print_LED-Photodiode-Support.stl)

Assemble the parts according to the instructions provided in the [Assembly Manual](structure_assembly_guide.md).

## Step 4: Upload the Arduino Code

1. Open the `.ino` file in the Arduino IDE.
2. Connect your Arduino board to the computer.
3. Select the correct board and port in the Arduino IDE.
4. Upload the code to the Arduino board.

## Step 5: Calibration

Follow the calibration protocol described in the [Calibration Guide](calibration.md) to ensure accurate measurements:

1. Prepare the calibration standards.
2. Adjust the device settings according to the calibration data.
3. Verify the calibration by testing with known samples.

## Troubleshooting

If you encounter any issues during the assembly or operation of the device, open an issue in the repository.

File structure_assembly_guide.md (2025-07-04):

# Assembly Guide for Support Structures

This guide provides detailed instructions on how to assemble the Chlorophyll-Fluorometer structures.

## Prerequisites

Before starting the assembly process, ensure you have the following tools and components ready:

- Components from the [Components List](hardware/components.md)
- PVC glue
- Sandpaper
- PVC stripper
- Laser cutter
- Screws, nuts, washers, spacers
- Paper towel or rag
- Wires (red and black)
- Soldering station

## Step 1 : Assemble the LEDs and photodiode support

Start by soldering wires to the LEDs and photodiode terminal. Pay attention to the polarity of the terminals : you can solder a red wire on the + terminals of the LED and the cathode terminal of the photodiode. A black wire can be soldered on the - terminals of the LEDs and on the anode of the photodiode.

When this is done, you can assemble de following components :
- Two LEDs
- Photodiode
- (Red filter : 16 x 20 mm) X3
- 3D printed support

<p align="center">
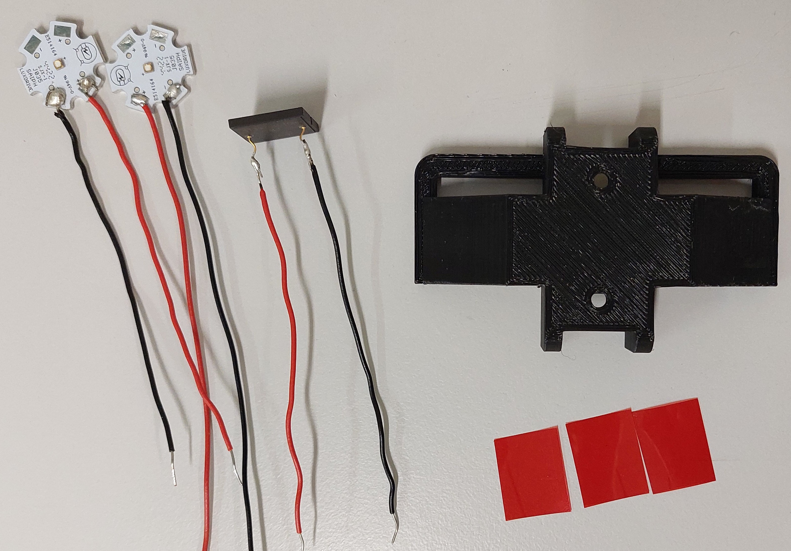
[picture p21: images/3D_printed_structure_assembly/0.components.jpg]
0.components
  
</p>

1. Position the LEDs in their slots. If they don't fit, you can lightly file the LEDs bases. The LEDs must be perfectly held by the support and must not move. The wires must come out of the back of the bracket.

<p align="center">
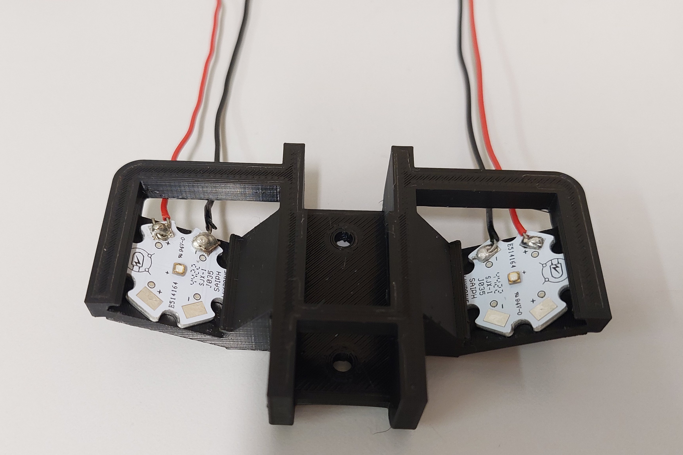
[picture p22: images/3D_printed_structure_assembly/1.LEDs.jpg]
1.LEDs
  
</p>

2. Position the photodiode in its slot. Bend the wires to make them come out of the back of the bracket.

<p align="center">
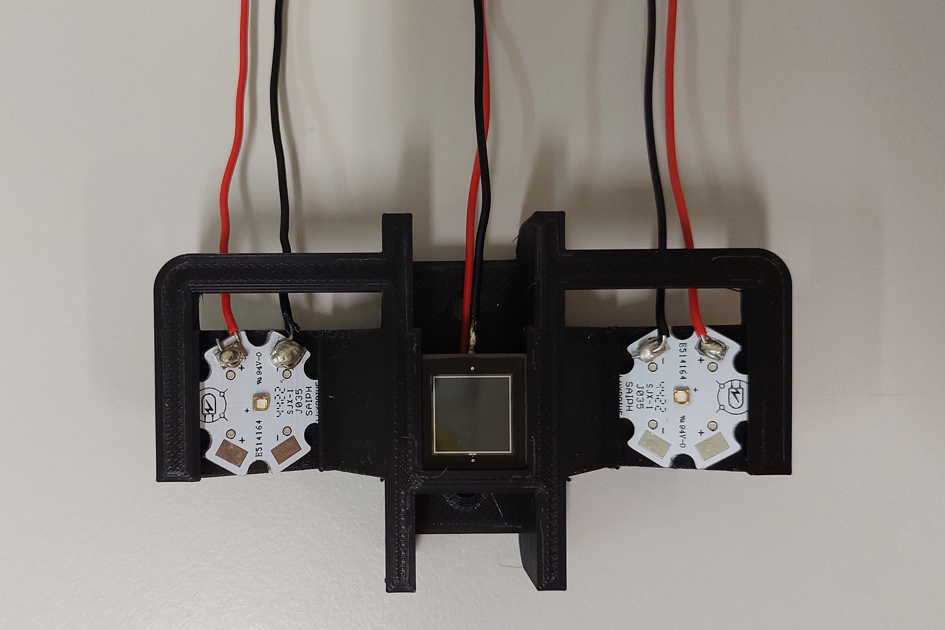
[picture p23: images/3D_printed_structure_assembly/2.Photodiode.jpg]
2.Photodiode
  
</p>

3. Add the three pieces of red filter. You can slide them in the photodiode slot, this will hold everything in place in the holder. However, make sure that the filters are perfectly flat on the photodiode, or light could pass underneath. You can add a small piece of scotch tape to the end of the filters and fold it over the photodiode so that nothing escapes.

<p align="center">
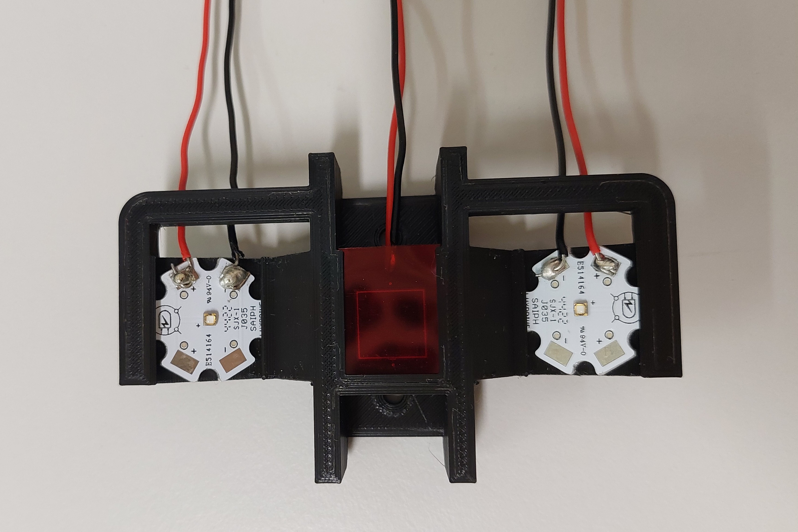
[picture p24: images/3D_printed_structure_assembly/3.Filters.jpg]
3.Filters
  
</p>

## Step 2 : Assemble the internal structure

The materials required for this step are :
- The Arduino UNO R3 board
- The PCB board with all the electronic components (Screen, SD Card shield)
- 4 spacers of 5 mm
- 4 screws, diameter 3 mm, length 5 mm + nuts
- 16 spacers of 30 mm
- 4 countersunk screw, diameter 3 mm, length 8 mm + nuts + washers
- 2 screws, diameter 3 mm, length 10 mm + nuts + washers
- 2 screws, diameter 2 mm, length 12 mm + nuts + washers
- A powerbank (100 x 50 x 2.5) mm max
- A dual output power supply and angled USB output cable
- The LEDs and photodiode support made in the previous step
- Matt black PMMA sheet, thickness 3 mm
- PMMA sheet, thickness 2 mm
- Screwdriver
- Laser cutter

<p align="center">
  0.components
</p>

1. Cut the structure in the PMMA sheets with the laser cutter. In 2 mm PMMA, cut the [top plate](hardware/Ready_to_laser_cut_Top-Plate.svg). In black PMMA, cut the [face and bottom plates](hardware/Ready_to_laser_cut_Structure-Plans.svg).

<p align="center">
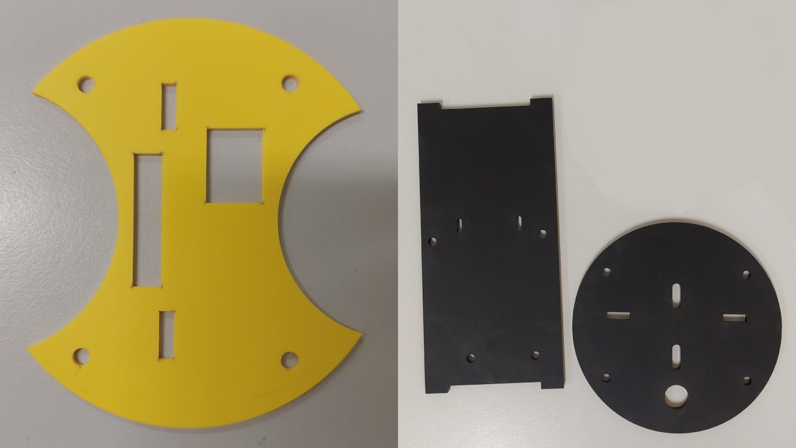
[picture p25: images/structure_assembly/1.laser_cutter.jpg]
1.laser_cutter
  
</p>

2. Screw 3 screws and 5 mm spacers to the Arduino board, as shown in the photo below. Connect the PCB to the Arduino board.

<p align="center">
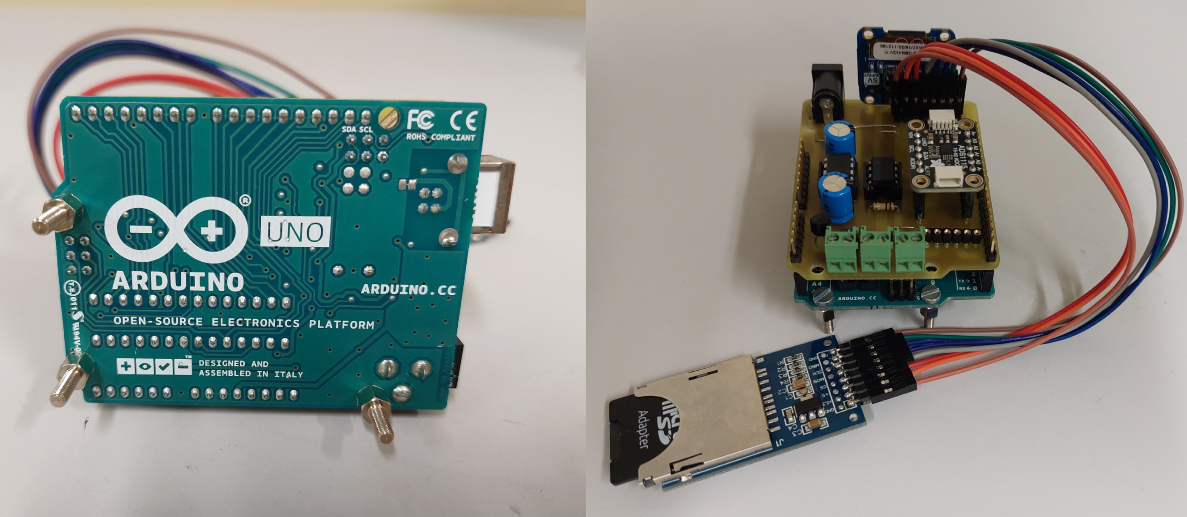
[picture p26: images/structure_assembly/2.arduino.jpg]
2.arduino
  
</p>

3. Take the face plate. Locate the side where the Arduino board goes. On the opposite side, screw the SD Card shield. Put a washer between the shield and the plate. The screws must protrude from the side of the module. You can loosen the nuts slightly, the height of the module will then be adjusted. Add a screw and a 5 mm spacer in the hole at the bottom left of the module.

<p align="center">
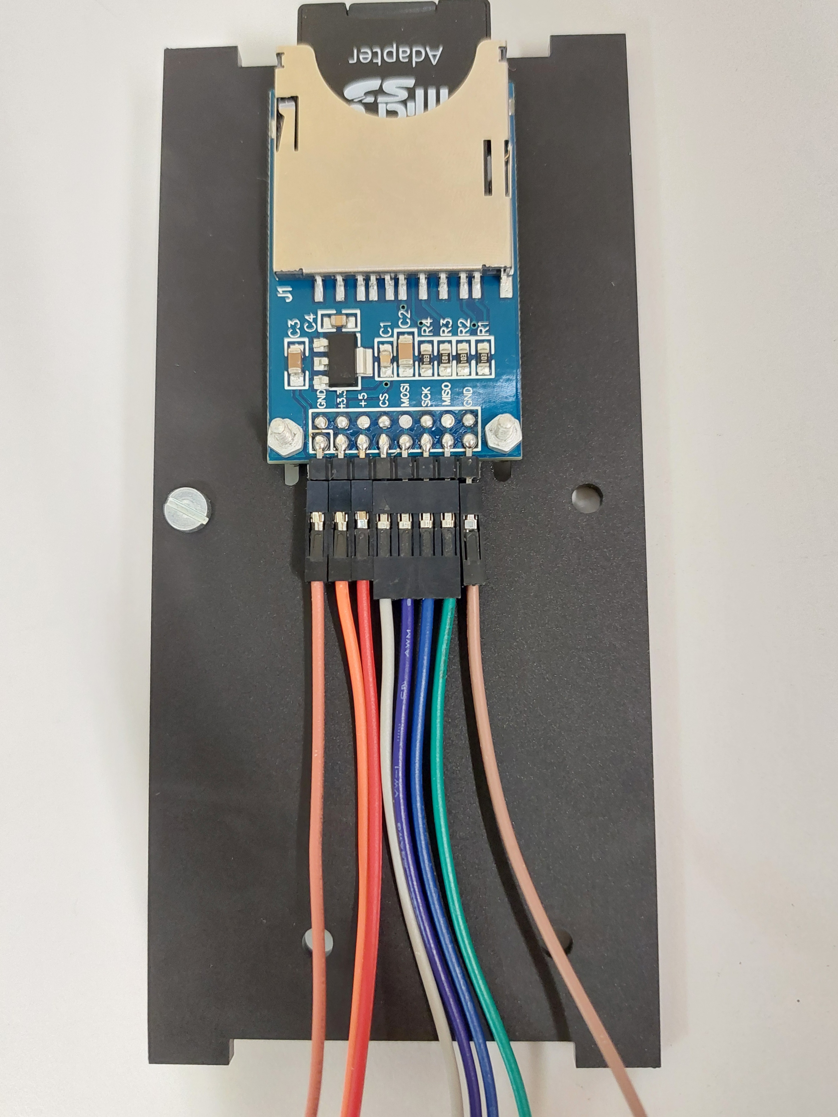
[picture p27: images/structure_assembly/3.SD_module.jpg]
  
</p>

4. Screw the Arduino board on the opposite face of the plate.

<p align="center">
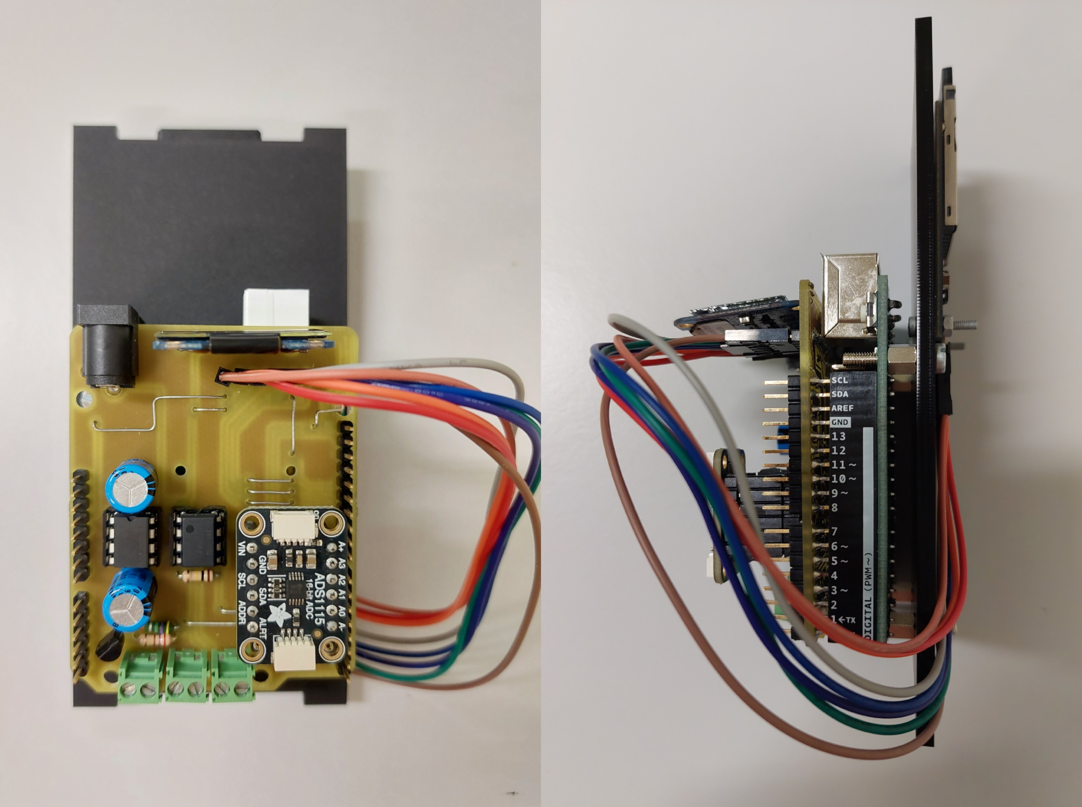
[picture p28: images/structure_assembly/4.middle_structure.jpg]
4.middle_structure
  
</p>

5. Take the bottom plate and the LEDs and photodiode support. Screw the LEDs and photodiode support under the bottom plate. Make sure that the large hole in the plate is on the same side as the wires. You can loosen the nuts for now, the position of the support will be adjusted. Pass the wires through the hole.

<p align="center">
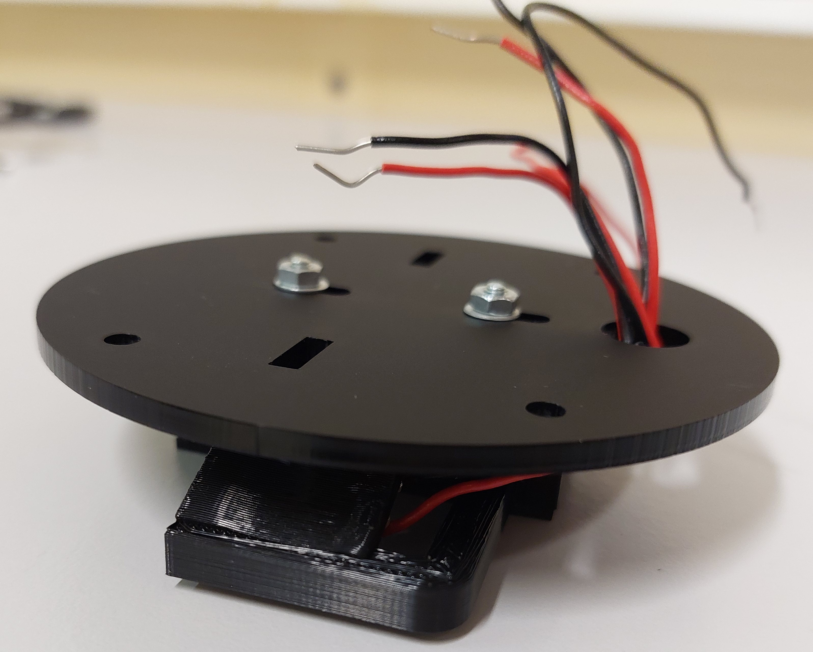
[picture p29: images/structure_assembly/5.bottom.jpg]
5.bottom
  
</p>

6. Take a plug. Adjust the position of the support. It should be in the center of the plug, and so should the plate. When the positions are correct, tighten the screws.

<p align="center">
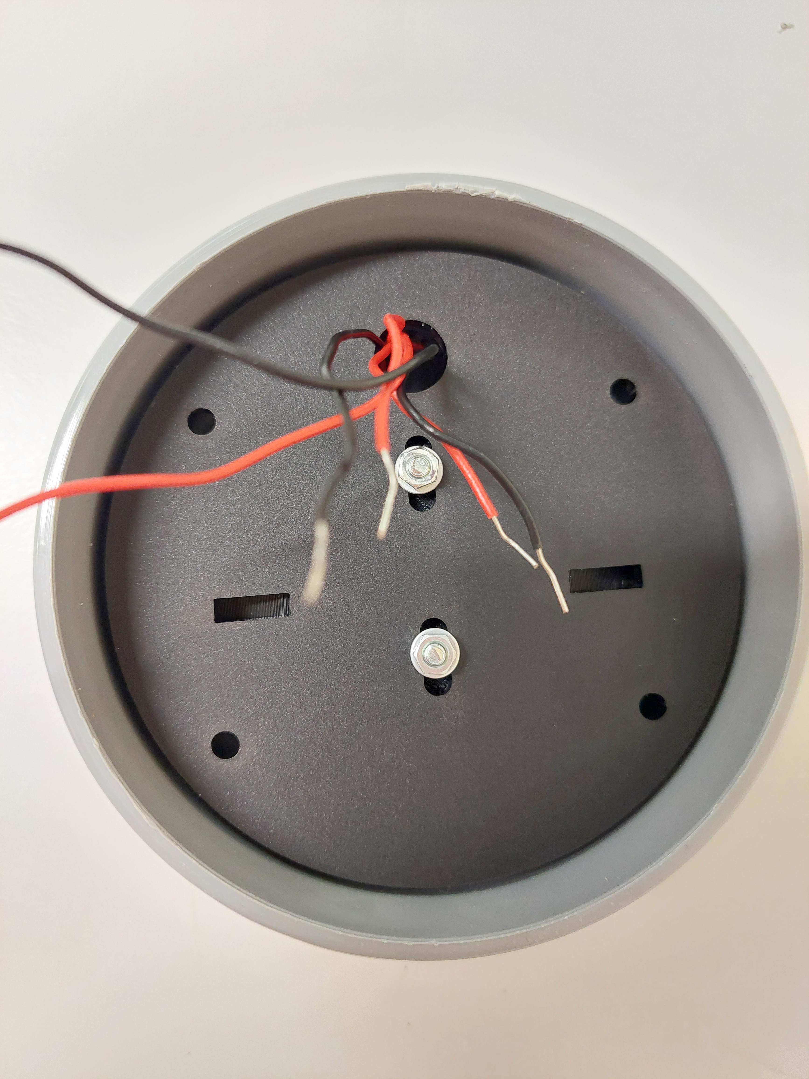
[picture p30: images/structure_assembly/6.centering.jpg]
6.centering
  
</p>

7. Screw the spacers into the four corners.

<p align="center">
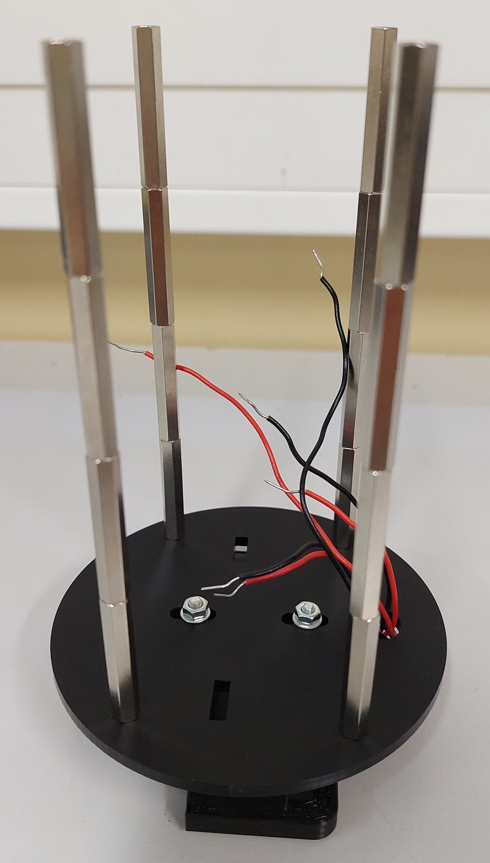
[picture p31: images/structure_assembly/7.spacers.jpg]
7.spacers
  
</p>

8. Screw the LEDs and photodiode wires into terminal strips of the PCB.

<p align="center">
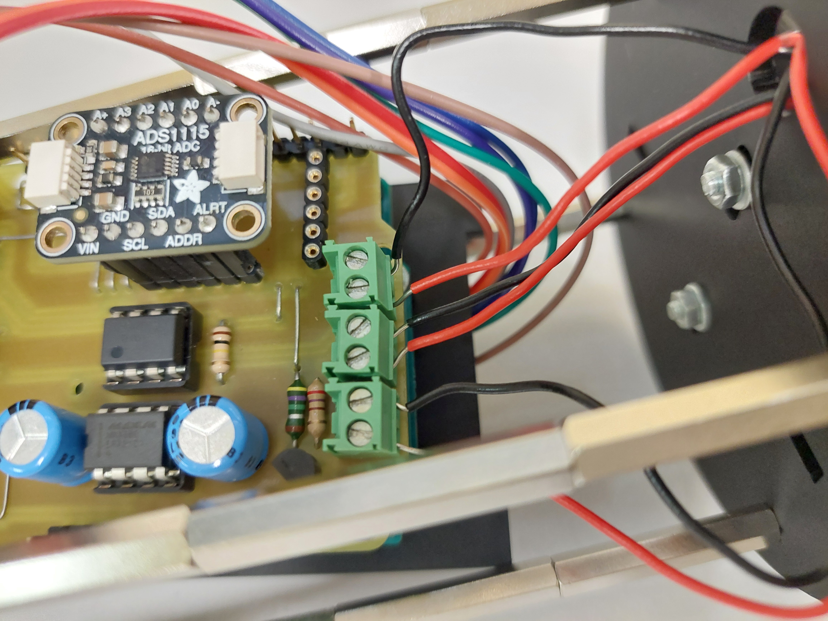
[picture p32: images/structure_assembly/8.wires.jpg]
8.wires
  
</p>

9. Put the face plate in the bottom plate, bend the wires of the LEDs and photodiode. Make sure the LEDs and photodiode didn't move in the process.

<p align="center">
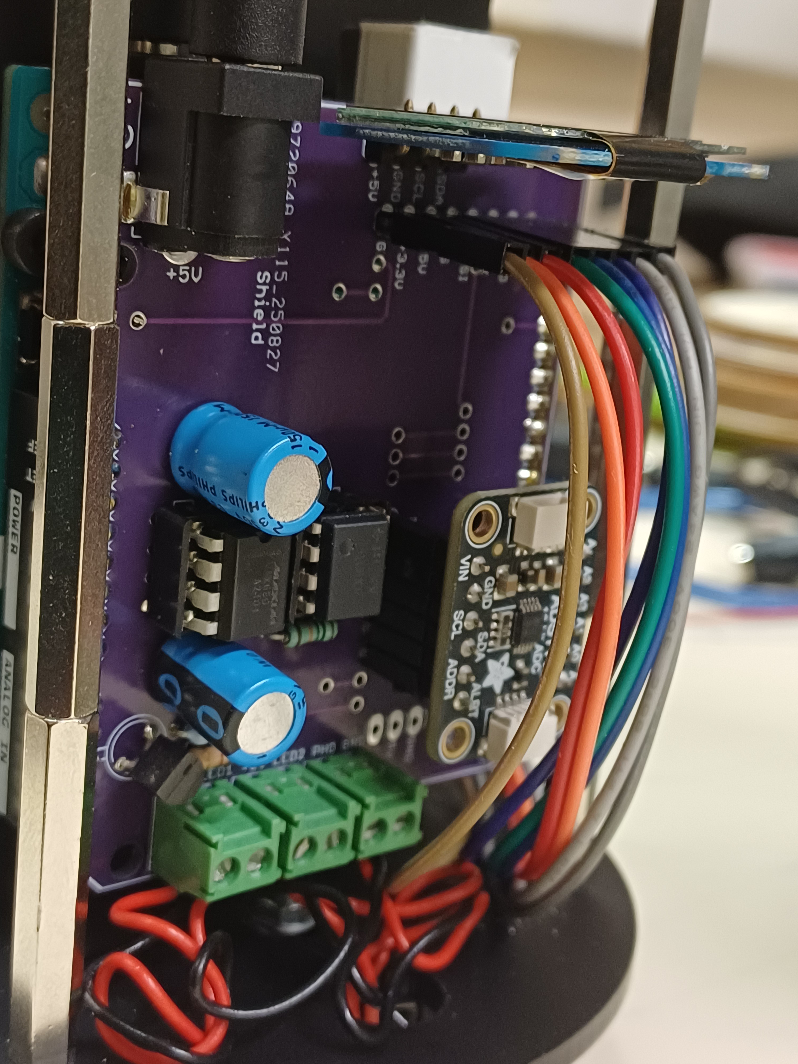
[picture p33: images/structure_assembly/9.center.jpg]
9.center
  
</p>

10. Screw the top plate. You can now adjust the position of the SD card shield so that it can be removed easily, but without protruding too far. Tighten the screws when the position is good.

<p align="center">
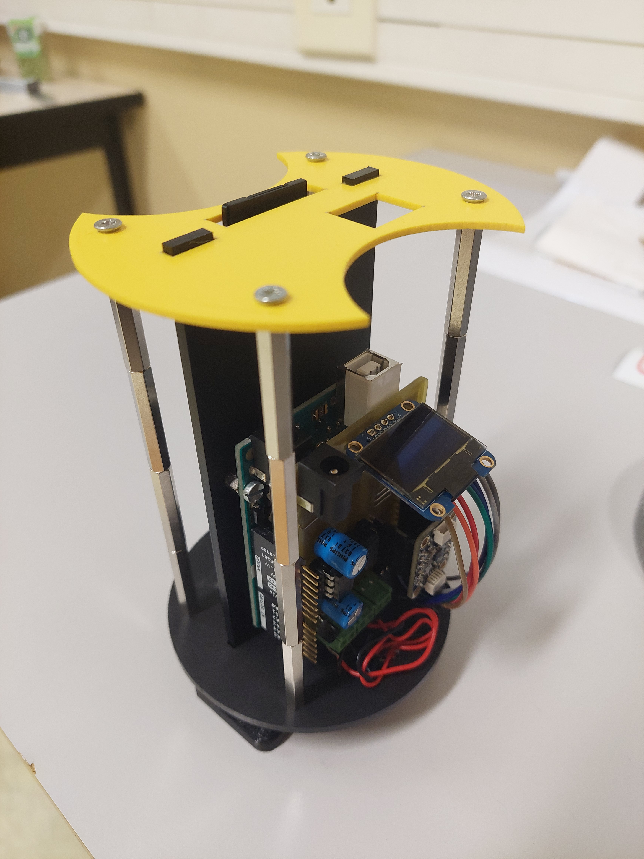
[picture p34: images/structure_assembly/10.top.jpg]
10.top
  
</p>

11. Put the powerbank and the alimentation cable.

<p align="center">
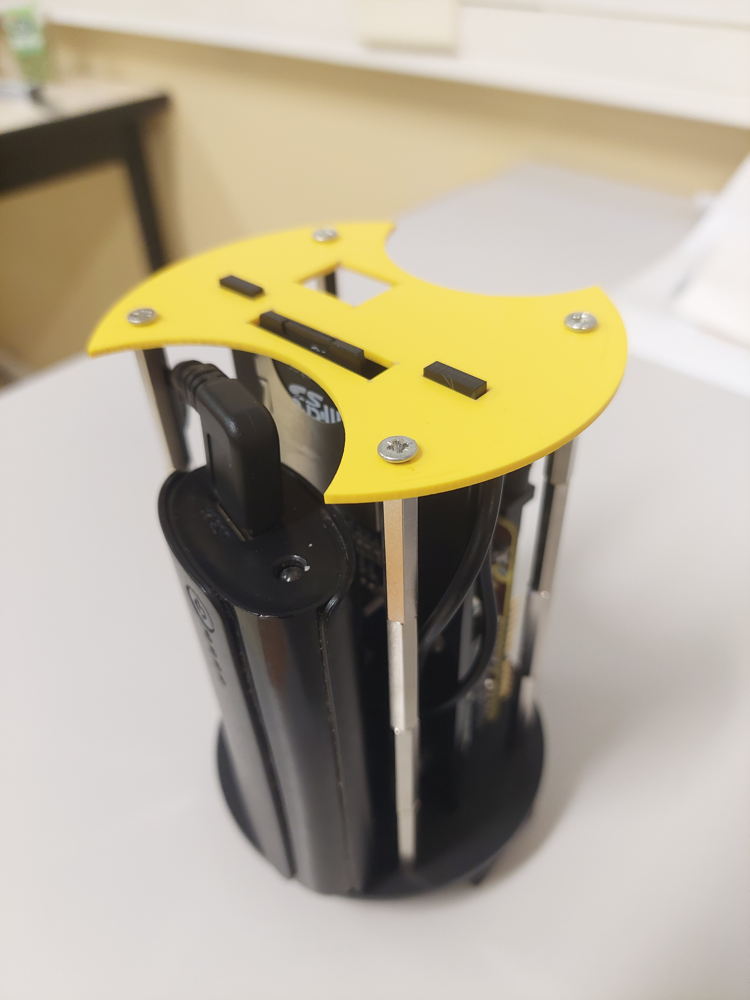
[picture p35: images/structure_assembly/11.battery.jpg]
11.battery
  
</p>

## Step 3 : Assemble the waterproof box

In this step, you will need :
- PVC sleeve
- Two PVC inspection plugs
- transparent PMMA plate
- PVC glue
- Sandpaper
- PVC stripper
- Laser cutter
- Paper towel or rag
- Ø89 mm and Ø84 mm hole saws
- Angle grinder

<p align="center">
  0.components
</p>

1.  Cut out the inside of the plugs, one with the 89 mm in diameter hole saw, and the other with the 84 mm in diameter hole saw. Make sure the holes are at the center of the plugs. Using a laser cutter, cut two PMMA discs, one 96.5 mm in diameter, the other 82.5 mm in diameter. The disc of 82.5 mm diameter needs to be sanded to fit perfectly in the plug. Using an angle grinder, sand one edge of the disc.

<p align="center">
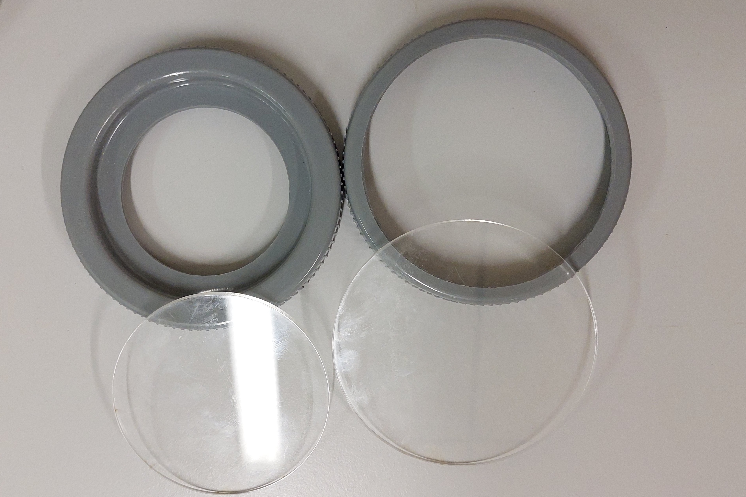
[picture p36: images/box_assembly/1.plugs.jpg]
1.plugs
  
</p>

2.  Glue the PMMA discs to the plugs : the smallest disc goes into the plug with the smallest hole, on the outside. The largest disc goes into the plug with the largest hole, on the inside of the plug. To glue, start by sanding the surfaces to be glued, then clean them with paint stripper. Apply a generous amount of glue to each surface, and press the pieces together firmly. Leave to dry for at least an hour. Then you can test the watertightness of the adhesive by placing the plugs on the surface of the water. If they float and there is no seepage, the bond is correct.

<p align="center">
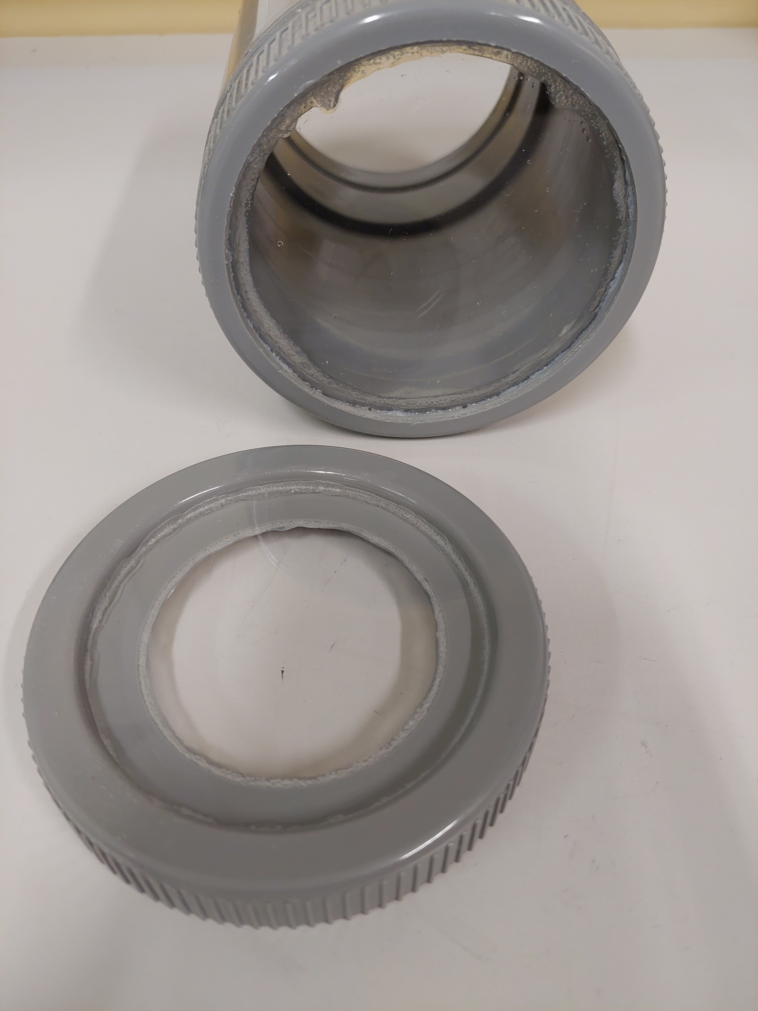
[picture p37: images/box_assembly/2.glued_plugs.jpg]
2.glued_plugs
  
</p>

3. Glue the rings for screwing on plugs to the sleeve. As above, sand the surfaces to be glued, then clean them. Apply a generous amount of glue. Leave to dry for at least an hour. You can test for leaks on either side by screwing on the plug with the smallest window and dipping the sleeve halfway into the water. If there is no infiltration, the bond is correct.

<p align="center">
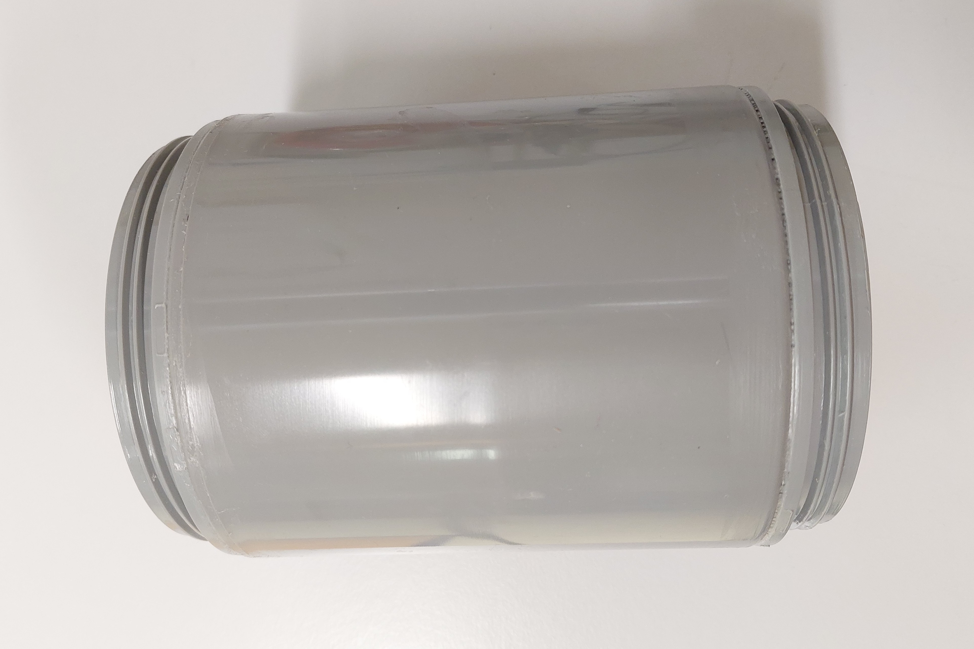
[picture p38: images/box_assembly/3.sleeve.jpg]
3.sleeve
  
</p>

4. Glue the plug with the largest window to one side of the sleeve. Apply a generous amount of glue to the threads of the sleeve and plug. Also apply glue to the gap between the sleeve and the plug, on the outside of the sleeve and on the indside, between the PMMA disc and the sleeve. Leave to dry for several hours. Test for leaks by immersing the sleeve halfway in water. If there are any leaks, add glue to the inside and/or outside of the sleeve where the leaks are. Allow to dry again and try again. You may need to repeat the operation several times until the seal is perfect.

<p align="center">
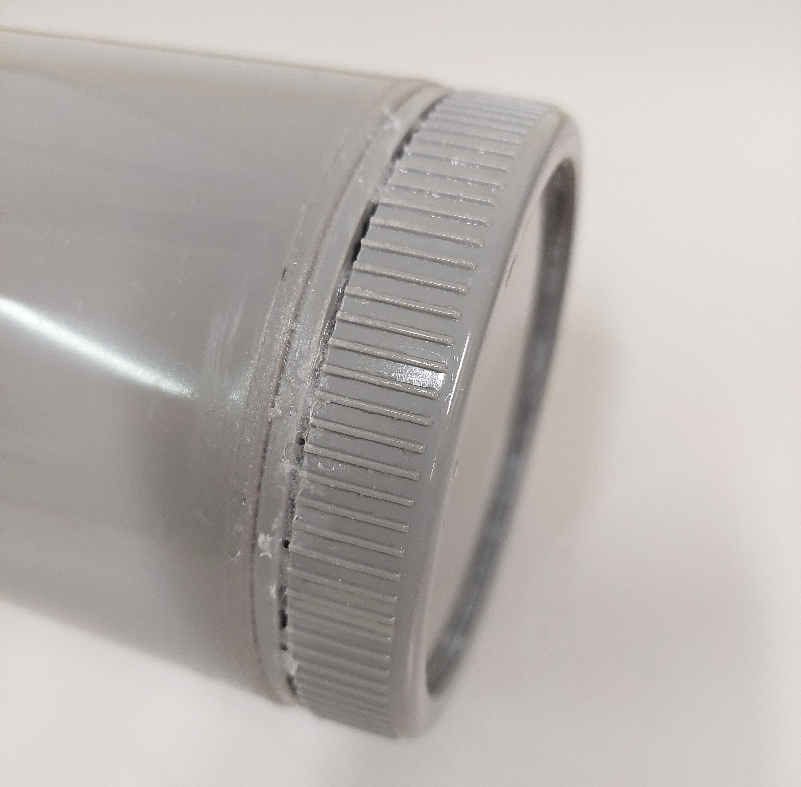
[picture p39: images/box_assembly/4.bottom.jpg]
4.bottom
  
</p>

The box is waterproof. The glued plug is the bottom, where LEDs and photodiode are located. The removable plug is on the top. Make sure that the seal is still present in the top cap when you close it, overwhise it may not be waterproof.

## Step 4 : Assemble the fluorometer

Slide the internal structure into the box. It must be at the bottom and must not move. Switch on the battery, and close the box.

<p align="center">
  Final_prototype
</p>
<p align="center">
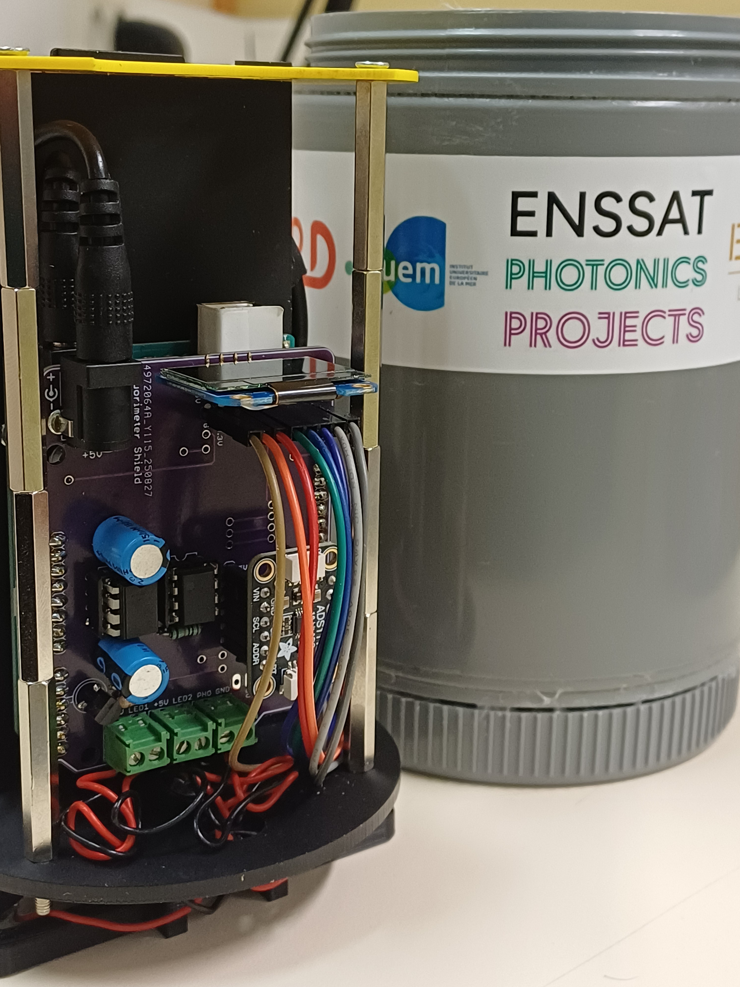
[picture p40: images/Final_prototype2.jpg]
Final_prototype2
  
</p>

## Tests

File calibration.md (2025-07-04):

# Calibration Guide for Chlorophyll-Fluorometer

This guide provides detailed instructions on how to calibrate the Chlorophyll-Fluorometer device.

## Prerequisites

Before starting the calibration process, ensure you have the following tools and components ready:

- The fluorometer completely closed and waterproof
- Various chlorophyll solutions of known concentration (minimum four solutions to ensure quality calibration)
- A container in which to immerse the fluorometer. Choose the container carefully : the material and shape can interfere with measurements. To choose the best container, fill it with water and measure the current in the water. The lowest current corresponds to the best container.
- Make your measurements in a dimly lit room, on a dark non-fluorescent surface.

## Step 1: Threshold in the dark

1. Put the fluorometer in a completely dark room, you can also use a black screen to hide completely the photodide.
2. Read the current value on the screen or via Bluetooth.

This value is the noise of the complete device.

## Step 2: Minimum value

1. Put clear water, if possible distilled water, in your container.
2. Dip the fluorometer in the water, make sure that there is no air between the window of the fluorometer and the surface of the water.
3. Read the current value.

This value is the minimum value that you should read, corresponding to a chlorophyll concentration of 0 µg/L. It will be the origin of your calibration line.

## Step 3: Calibration with chlorophyll solutions

1. Remove water from container, then put the first chlorophyll solution (with the smaller concentration) in the container.
2. As above, dip the fluorometer in the solution, check for air bubbles.
3. Read the current value.

This value corresponds to the concentration you tested. 

4. Repeat this process for all the solutions you have, increasing the concentration.

## Step 4: Draw the calibration line

1. Draw your measures in a data analysis and visualization program. On the x-axis put the concentration, on the y-axis put the current.
2. Fit the points with a linear model. You can adjust the ordinate at origin with the value you read in **Step 2**.

For concentrations between 1 and 50 µg/L, you should get a line similar to the figure below :

<p align="center">
  calibration_line
</p>

Your fluorometer is now calibrated.

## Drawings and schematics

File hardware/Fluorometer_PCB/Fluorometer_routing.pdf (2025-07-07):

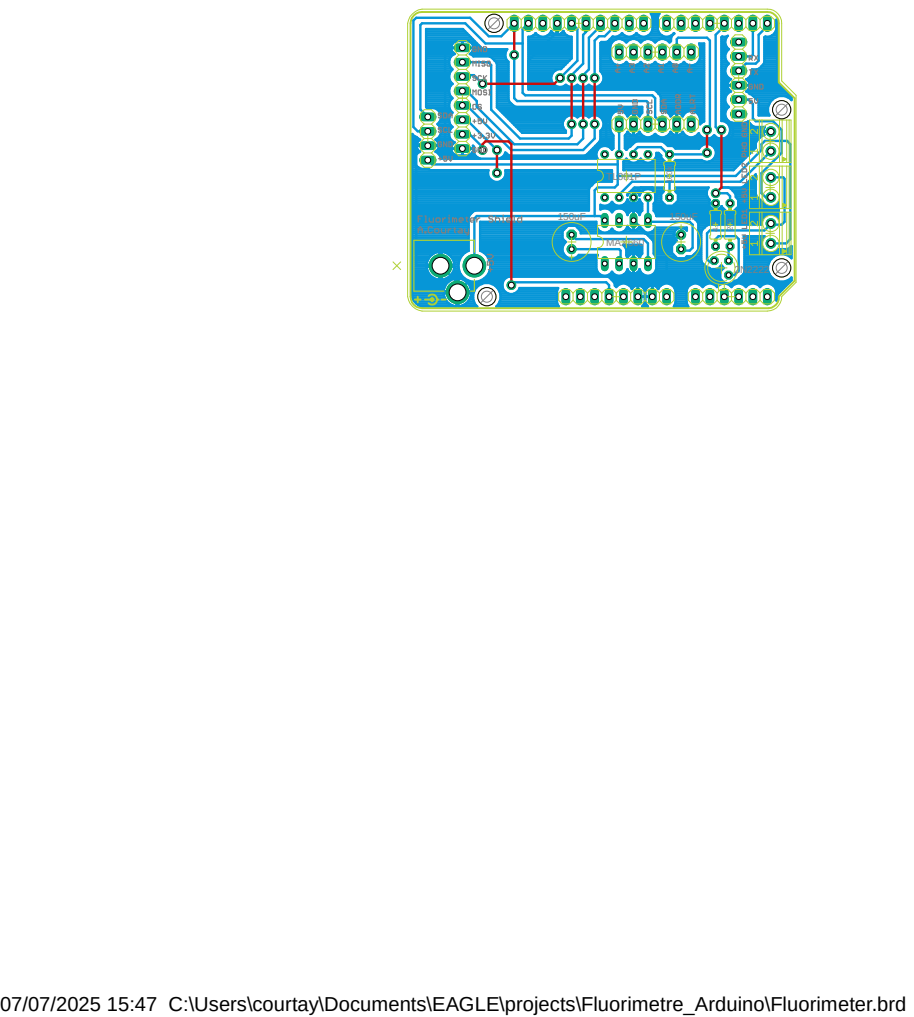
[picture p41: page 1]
MAX660

07/07/2025 15:47 C:\Users\courtay\Documents\EAGLE\projects\Fluorimetre_Arduino\Fluorimeter.brd

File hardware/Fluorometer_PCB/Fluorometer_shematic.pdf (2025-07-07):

1 | 2 | 3 | 4 | 5 | 6 | 7 | 8

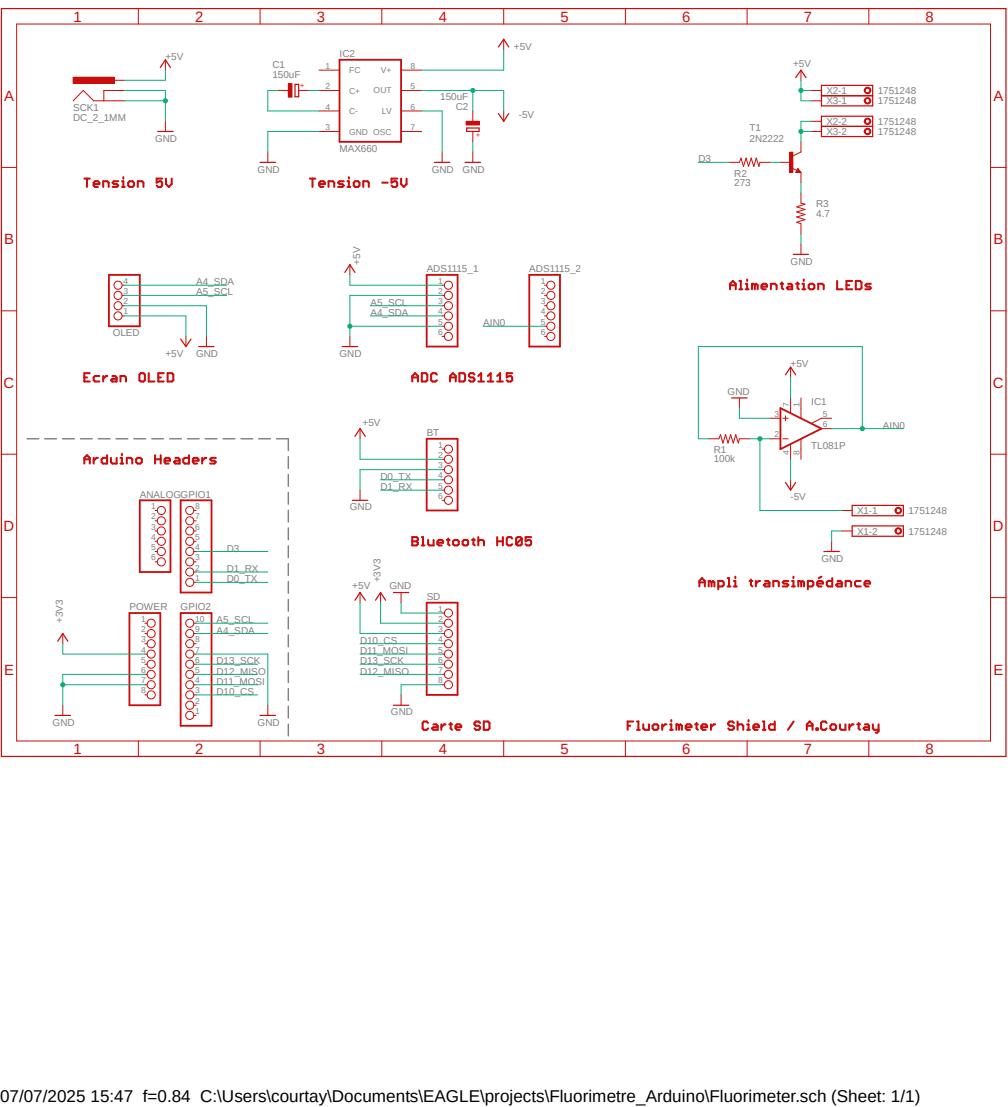
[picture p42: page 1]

07/07/2025 15:47 f=0.84 C:\Users\courtay\Documents\EAGLE\projects\Fluorimetre_Arduino\Fluorimeter.sch (Sheet: 1/1)

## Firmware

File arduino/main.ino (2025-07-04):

#include <Wire.h>
#include <Adafruit_ADS1X15.h>
#include "U8glib.h"
#include "SPI.h"
#include "SD.h"

// === Display Setup ===
U8GLIB_SSD1306_128X64 u8g(U8G_I2C_OPT_NONE);

// === ADC ===
Adafruit_ADS1115 ads;

// === Sampling & LED ===
const int ledPin = 3;
volatile bool sampleNow = false;
volatile bool inSamplingWindow = false;

bool ledState = false;
unsigned long lastWindowStart = 0;
unsigned long interruptCount = 0;

// === Signal Processing ===
float lowSample = 0;
bool lowSampleReady = false;
const int MA_WINDOW = 8;
float maBuffer[MA_WINDOW];
int maIndex = 0;
int maCount = 0;
float filteredSum = 0;
int filteredCount = 0;
const int maxFiltered = 200;

// === SD Card Shield ===
File currents;
const int chipSelect = 4;  

void setup() {
  pinMode(ledPin, OUTPUT);
  digitalWrite(ledPin, LOW);

   Serial.begin(115200); // Optional debug

// === Display Init ===
  u8g.firstPage();
  do {
    u8g.setColorIndex(1); // 1 for white text on black background
    u8g.setFont(u8g_font_7x14); // simple font
    u8g.drawStr(0,12,"Starting...");
  } while (u8g.nextPage());
  delay(1000);

  // === ADC Init ===
  ads.begin();
  ads.setGain(GAIN_ONE);
  ads.setDataRate(128);

  // === Timer2 for ~128Hz ===
  cli();
  TCCR2A = (1 << WGM21);
  TCCR2B = (1 << CS22); // 64 prescaler
  OCR2A = 249;          // ~128Hz
  TIMSK2 |= (1 << OCIE2A);
  sei();

  // === SD Card Shield Init ===
  pinMode(SS, OUTPUT);
  if (!SD.begin(SPI_HALF_SPEED, chipSelect)) { 
    u8g.firstPage();
    do {
      u8g.setFont(u8g_font_7x14);
      u8g.setPrintPos(1, 12);
      u8g.print("SD initialization");
      u8g.setPrintPos(1, 24);
      u8g.print("failed");
    } while (u8g.nextPage());
    delay(10000);}

  currents = SD.open("currents.txt", FILE_WRITE);
  if (currents) {
    currents.println("Time (ms) Current (nA)");
    currents.close();
  } else {
    u8g.firstPage();
    do {
      u8g.setFont(u8g_font_7x14);
      u8g.setPrintPos(1, 12);
      u8g.print("error opening");
      u8g.setPrintPos(1, 24);
      u8g.print("currents.txt");
    } while (u8g.nextPage());
    delay(10000);}
  
  lastWindowStart = millis();
}

void loop() {
  unsigned long now = millis();

  // === Start Sampling Window ===
  if (!inSamplingWindow && (now - lastWindowStart >= 3000)) {
    inSamplingWindow = true;
    lastWindowStart = now;
    filteredSum = 0;
    filteredCount = 0;
    maIndex = 0;
    maCount = 0;
    lowSampleReady = false;
    u8g.firstPage();
    do {
    u8g.setPrintPos(1, 14);
    u8g.setFont(u8g_font_helvR14);
    u8g.print("Sampling...");
    } while (u8g.nextPage());
    delay(500);
  }

  // === End Sampling Window ===
  if (inSamplingWindow && (now - lastWindowStart >= 1000)) {
    inSamplingWindow = false;
    PORTD &= ~(1 << PORTD3);  // LED OFF
    ledState = false;

    if (filteredCount > 0) {
      //float avg = filteredSum / filteredCount; // voltage value
      float avg = (filteredSum / filteredCount)*10000;
      u8g.firstPage();
      do {
      u8g.setPrintPos(1, 14);
      u8g.setFont(u8g_font_helvR14);
      //u8g.println("Avg V : "); //print voltage value
      u8g.println("Avg nA : ");
      u8g.setPrintPos(1, 35);
      u8g.print(avg);
      } while (u8g.nextPage());
      currents = SD.open("currents.txt", FILE_WRITE);
      currents.print(now);
      currents.print(" ");
      currents.println(avg);
      currents.close();
    } else {

      u8g.firstPage();
      do {
        u8g.setPrintPos(1, 14);
        u8g.setFont(u8g_font_helvR14); 
        u8g.print("No data");
      } while (u8g.nextPage());
    }
    delay(1000);
  }

  // === Sampling Logic ===
  if (sampleNow && inSamplingWindow) {
    sampleNow = false;

    ledState = !ledState;
    if (ledState)
      PORTD |= (1 << PORTD3);
    else
      PORTD &= ~(1 << PORTD3);

    int16_t adc = ads.readADC_SingleEnded(0);
    float voltage = calculateVoltage(adc);

    // Adjust gain only on HIGH state
    if (ledState) adjustGain(voltage);

    if (!ledState) {
      lowSample = voltage;
      lowSampleReady = true;
    } else if (lowSampleReady && filteredCount < maxFiltered) {
      float signal = abs(voltage - lowSample);
      lowSampleReady = false;

      maBuffer[maIndex] = signal;
      maIndex = (maIndex + 1) % MA_WINDOW;
      if (maCount < MA_WINDOW) maCount++;

      float maSum = 0;
      for (int i = 0; i < maCount; i++) maSum += maBuffer[i];
      float smoothed = maSum / maCount;

      filteredSum += smoothed;
      filteredCount++;
    }
  }
}

// === ISR: 128 Hz Sampling ===
ISR(TIMER2_COMPA_vect) {
  sampleNow = true;
  interruptCount++;
}

// === Gain Compensation Voltage Calculation ===
float calculateVoltage(int16_t adc) {
  switch (ads.getGain()) {
    case GAIN_SIXTEEN: return adc * 0.256 / 32768.0;
    case GAIN_EIGHT:   return adc * 0.512 / 32768.0;
    case GAIN_FOUR:    return adc * 1.024 / 32768.0;
    case GAIN_TWO:     return adc * 2.048 / 32768.0;
    case GAIN_ONE:     return adc * 4.096 / 32768.0;
    default:           return adc * 4.096 / 32768.0;
  }
}

// === Auto Gain Adjustment on HIGH Samples Only ===
void adjustGain(float voltage) {
  if (voltage < 0.2)
    ads.setGain(GAIN_SIXTEEN);
  else if (voltage < 1.0)
    ads.setGain(GAIN_FOUR);
  else if (voltage < 2.0)
    ads.setGain(GAIN_TWO);
  else
    ads.setGain(GAIN_ONE);
}

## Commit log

2025-06-12 Update documentation links and remove redundant content
    - Fixes a broken link to the PCB design file in the assembly guide.
    - Removes unused or redundant content from README.md and calibration.md.
    - Enhances clarity and maintains consistency in documentation.
2025-06-18 Create assembly_structures_guide
2025-06-27 Update and rename assembly_structures_guide.md to structure_assembly_guide.md
2025-10-03 updated components list + image with A.Courtay shield
    [Fluorometer.brd, Fluorometer.sch]
2025-10-03 removed unused files before pull request
    [Fluorometer.brd, Fluorometer.sch]
2025-10-06 updated assembly guide with PCB manufacturer info
2025-11-06 updated capacitor ref in components list
